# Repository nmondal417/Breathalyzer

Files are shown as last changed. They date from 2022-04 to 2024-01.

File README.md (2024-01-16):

# Breathalyzer Project Overview

The overall goal of this project is to create a wireless device that can be used to analyze the breath of medical patients to diagnose various diseases. The underlying technology is a graphene FET array. When the graphene FETs come into contact with different gases, the properties of the FETs will change. For example, the IDS vs VGS curve of the graphene FET may shift depending on the concentration of a certain gas molecule in the patient's breath. 

This GitHub project contains the PCBs and the code that are used to control and measure the graphene FET array. In simple terms, the PCB generates analog voltages VDS and VGS, and sends these to the graphene FET. Two multiplexers are used to select one particular FET out of the array. The PCB then measures the resulting IDS on that FET. This process is then repeated for every FET in the array, and then for different VDS and VGS. A python script can be used to plot the various voltage vs current curves.

functional_diagram

# Device Design

The device is split into two chambers. The top chamber contains the graphene FET chip, an interface PCB for connecting to the chip, a humdity sensor, and a heater to prevent condensation on the chip. The bottom chamber contains most of the control electronics, inlucding the ESP32 micronctroller, the amplifiers, and multiplexers. There is also a single-cell 2 Ah LiPo for powering all the electronics, and a boost converter for specifically powering the heater. The LiPo can be charged through the USB-C connector located on the bottom of the device; when charging, the device will automatically turn off. 

breathalyzer_drawing

On the outside of the device, there are various switches to control and LEDs to monitor the breathalyzer status. The main on switch connects the LiPo to the system and turns everything except the heater on; the heater on switch controls the heater. An RGB charge status LED lights up when the device is being charged; an orange light indicates that charging is occurring, while a white light indicates that charging is completed. Finally a "BLOW" LED controlled by the ESP32 indicates to the patient when they should blow into the device.

# PCBs

## ESP32 Carrier

https://github.com/nmondal417/Breathalyzer/tree/main/New%20PCB/Breathalyzer_ESP32

This PCB is where the ESP32, the main microcontroller, mounts **(NOTE: make sure to place the ESP32 correctly! the USB connector should face the side labeled "FRONT")**. The ESP32 controls the DAC, the ADC, and the multiplexers. It can also read data from the humidity sensor and the heater thermistor. It reports the current measurements in either serial or Bluetooth serial. 

The carrier board also contains the LiPo charge controller, the USB-C charging port, and the main 3.3V regulator that powers most of the ICs. All of the buttons and switches plug into the ESP32 carrrier board.

## Amplifier

https://github.com/nmondal417/Breathalyzer/tree/main/New%20PCB/Breathalyzer_Power%2BICs

This PCB contains the DAC, the ADC, and the op-amps that amplify the gate voltages.

The DAC (AD5328) communicates with the ESP32 over SPI. The DAC generates 6 gate voltages and 1 drain voltage. These voltages are in the range of 0 to 2 V; however, since the source voltage of this system is 1 V, the VGS and VDS voltages are actually -1 to +1 V. 

The op-amps then buffer and amplify the gate voltages. The op-amps can either provide x1 amplification (where it just acts a buffer), or x10 amplifcation. This amplification is controlled by the ESP32. The ESP32 controls two solid-state switches (ADG5433), which can change the amplifer gain by switching in a feedback resistor connected across the op-amp. The post-amplifcation gate voltage can be from -10 to +10 V.

The ADC (AD7274) communicates with the ESP32 over SPI. The ADC input is the voltage from the transimpedance amplifier. The ADC reads in range of 0 to 2V, and sends the ESP32 a 12-bit digital reading. 

This PCB also contains the 1V and 2V regulators that generate reference voltages for the DAC, ADC, and the op-amps, as well as a dual DC/DC converter (LT1945) that generates the -11V and +11V rails used for the amplifiers.

Finally, there is a mechanical switch that can completely disconnect the gate voltages from the graphene chip. This is useful for quickly turning off a voltage sweep, since if the incorrect gate voltages are accidentally applied the FET array can be destroyed.

## Multiplexer

https://github.com/nmondal417/Breathalyzer/tree/main/New%20PCB/Breathalyzer_Mux%2BConn

This PCB contains the two main multiplexers, the ribbon cable connector, and the transimpedance amplifier. 

The multiplexers are the ADG732. One is the drain demultiplexer, which sends the drain voltage to 1 of the 32 rows of the FET array. The other is the source muliplexer, which measures the source current from 1 of the 32 columns. 

The ribbon cable connector connects to the ribbon cable that runs from this PCB to the chip interface board. This cable is the PCB's connection to the drain, gate, and source terminals on the FET array.

The transimpedance ampliifer is an op-amp that is used to convert the source current measurement into a voltage. The formula is VMEAS = 1 - 1000*IDS, so an IDS of 100 uA would result in a VMEAS of 0.9V. This VMEAS is sent to the ADC.

# Code

All the code for this version of the breathlyzer is under 'New PCB code.' While the main code that runs on the ESP32 during normal operation is IV_Array_main_NEW, there are other files that test specific parts of the system, like the DAC and ADC, and are helpful for debugging.

## Blink

Simple test to just check if code can be uploaded correctly to the ESP32.

## ADC_DAC_test

This test can be used to test the ADC, DAC, or both together. Bascially, write analog voltages using the DAC and read an analog voltage using the ADC. If you are testing both the DAC and ADC at the same time, connect one of the DAC's output voltages to the input of the ADC.

## offset_and_gain_test

Used for checking and adjusting for the offset or gain error of the ADC and DAC. Test each DAC channel by connecting it to the ADC, and compare the read voltages to the expected values.

## gate_voltage_test

Tests that gate voltages can be generated properly. Combines the DAC code along with additional code to turn on the gate amplifier power supply and control the amplification.

## multiplexer_test

Close to a full system test, but instead of having the actual graphene array connected, you connect a test resistor between a drain connection on one mux and source connection on the other. When the correct select bits are sent to the muxes, the code should report the resistor value.

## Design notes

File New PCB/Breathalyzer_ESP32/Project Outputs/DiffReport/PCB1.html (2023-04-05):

Altium

# Differences Report for Project Breathalyzer_ESP32.PrjPcb and PCB1.PcbDoc

Date: | | 3/28/2023
Time: | | 11:31:12 PM
Filename: | | C:\college\UROP_S2022\Breathalyzer_ESP32\Project Outputs\DiffReport\PCB1.html

## Extra Room Definitions

Schematic Object | PCB Object
[Room ESP32 (Scope=InComponentClass('ESP32')) TopLayer]

Back to top

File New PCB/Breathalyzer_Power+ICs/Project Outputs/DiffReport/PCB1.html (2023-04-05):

Altium

# Differences Report for Project Breathalyzer_Power+ICs.PrjPcb and PCB1.PcbDoc

Date: | | 3/29/2023
Time: | | 1:41:04 PM
Filename: | | C:\college\UROP_S2022\Breathalyzer_Power+ICs\Project Outputs\DiffReport\PCB1.html

## Extra Room Definitions

Schematic Object | PCB Object
[Room Power+ICs (Scope=InComponentClass('Power+ICs')) TopLayer]

Back to top

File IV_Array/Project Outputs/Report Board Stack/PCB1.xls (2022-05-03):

Board Stack Report
Stack Up |  | Layer Stack
Layer | Rigid | Name | Material | Thickness | Constant
1 |  | Top Paste
2 |  | Top Overlay
3 |  | Top Solder | Solder Resist | 0.50mil | 3.3
4 |  | Top Layer | Copper | 0.70mil
5 |  | Dielectric 1 | PP-006 | 2.80mil | 4.1
6 |  | GND | Copper | 1.38mil
7 |  | Dielectric1 | FR-4 | 59.00mil | 4.3
8 |  | PWR | Copper | 1.38mil
9 |  | Dielectric 2 | PP-006 | 2.80mil | 4.1
10 |  | Bottom Layer | Copper | 0.70mil
11 |  | Bottom Solder | Solder Resist | 0.50mil | 3.3
12 |  | Bottom Overlay
13 |  | Bottom Paste
 | Height : 69.76mil

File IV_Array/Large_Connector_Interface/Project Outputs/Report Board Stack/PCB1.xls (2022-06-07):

Board Stack Report
Stack Up |  | Layer Stack
Layer | Rigid | Name | Material | Thickness | Constant
1 |  | Top Paste
2 |  | Top Overlay
3 |  | Top Solder | Solder Resist | 0.50mil | 3.3
4 |  | Top Layer | Copper | 0.70mil
5 |  | Dielectric1 | FR-4 | 59.00mil | 4.3
6 |  | Bottom Layer | Copper | 0.70mil
7 |  | Bottom Solder | Solder Resist | 0.50mil | 3.3
8 |  | Bottom Overlay
9 |  | Bottom Paste
 | Height : 61.40mil

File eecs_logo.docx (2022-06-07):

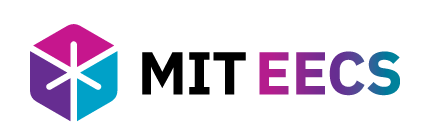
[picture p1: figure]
EECS Communication Lab

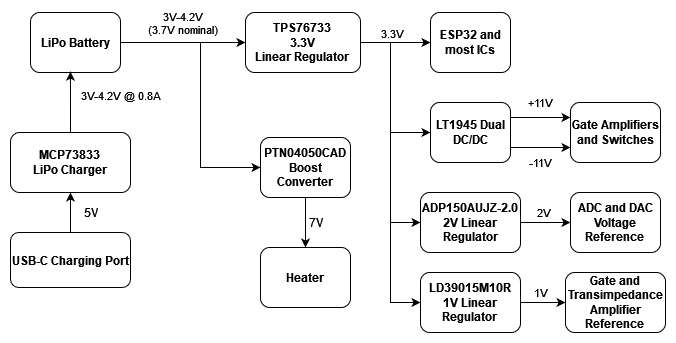
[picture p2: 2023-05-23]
power_flow.png

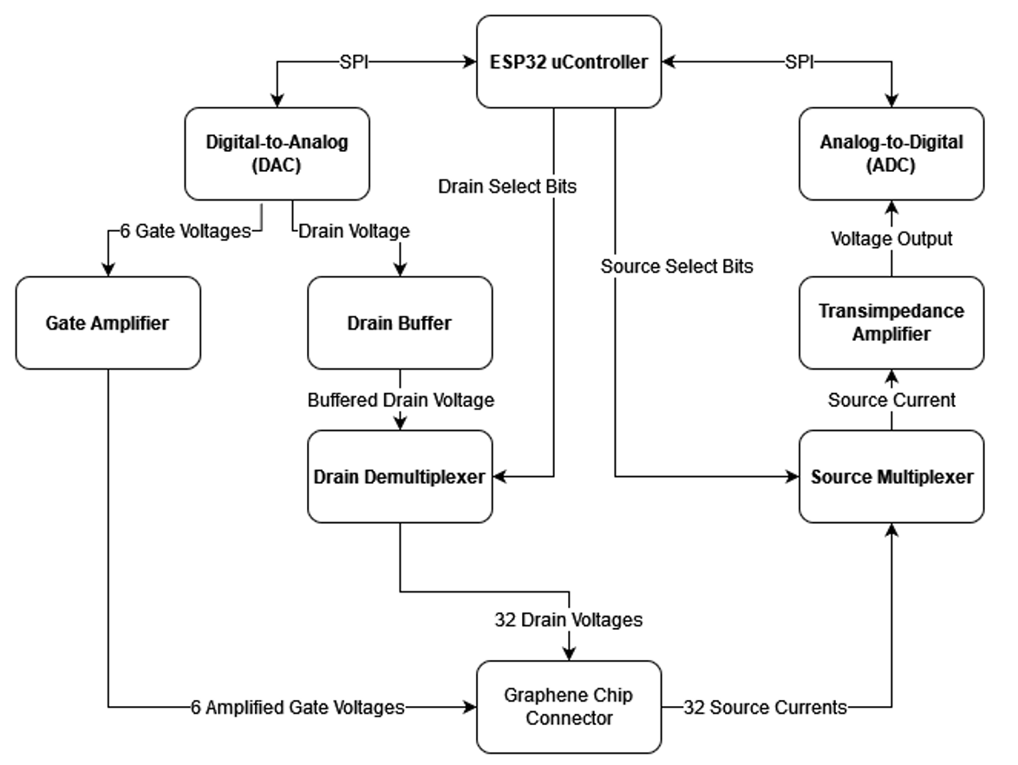
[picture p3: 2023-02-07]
functional_diagram.png

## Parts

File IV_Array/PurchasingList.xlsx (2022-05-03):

Comment | Description | Designator | Fitted | Footprint | LibRef | Quantity | Value | PN | OK? | #Bought
100 nF | CAP CER 0.1UF 50V X7R 0805 | C1, C2, C3, C4, C5, C12, C18, C19, C20, C21, C22, C23, C24, C25, C26, C27, C28 |  | FP-C0805C-DN-MFG | CMP-2007-00279-2 | 17 | 0.10 μF | C0805C104K5RACTU (https://octopart.com/c0805c104k5ractu-kemet-143926?r=sp) | Mouser | 100 | c
10 uF | CL21 Series 0805 10uF 25V ±10% Tolerance X5R Multilayer Ceramic Chip Capacitor | C6, C7, C8, C9, C10, C11 |  | FP-CL21-IPC_A | CMP-13271-002975-1 | 6 |  | CL21A106KAYNNNE | Mouser | 30 | c
100 pF | 08055C101KAT2A | C13 |  | CAPC2013X140X50ML20T25 | CMP-2007-04713-1 | 1 |  | 08055C101KAT2A (https://octopart.com/08055c101kat2a-kyocera+avx-41088415?r=sp) | Mouser | 10 | c
1 uF | C1206C105K5RACTU | C14, C16 |  | CAPC3216X110X50LL20T25 | CMP-2000-06011-1 | 2 |  | C1206C105K5RACTU | Mouser | 10 | c
4.7 uF | CAP CER 4.7UF 25V X5R 0805 | C15 |  | FP-C0805C475K3PACTU-MFG | CMP-2007-01010-2 | 1 |  | C0805C475J3RACTU | Mouser | 10 | c
4.7 pF | 08055A4R7CAT2A | C17 |  | CAPC2013X71X50ML20T25 | CMP-1036-00549-2 | 1 |  | 08055A4R7CAT2A | Mouser | 10 | c
MBR0530 | DIODE SCHOTTKY 30V 500MA SOD123 | D1, D2, D3 |  | FP-425-04-MFG | CMP-2000-05113-2 | 3 |  | MBR0530T1G | Mouser | 15 | c
FH12-36S-0.5SH_55_ | Connector | J2 |  | FH1236S05SH55 | FH12-36S-0.5SH_55_ | 1 |  |  | Already have
5015 | PC TEST POINT MINIATURE | J3, J4, J5, J6, J7, J8, J9, J11, J12, J13, J14, J15, J16, J17, J18 |  | FP-5015-MFG | CMP-2000-05183-2 | 15 |  |  | N/A
5600200620 | CONN HEADER SMD 6POS 2MM | J10 |  | FP-5600200620-MFG | CMP-04776-000066-1 | 1 |  | 560020-0620 | Mouser | 5 | c
FH28H-80S-0.5SH(05) | CONN FFC BOTTOM 80POS 0.50MM R/A | J19 |  | FP-FH28H-80S-0_5SH_05-MFG | CMP-11609-000031-1 | 1 |  |  | Already have
503366-6011 | 0.5 mm Pitch Easy-On(TM) FPC Connector, 2.0 mm Mated Height, Right Angle, SMT, Bottom Contact, 60 Circuits, -20 to 85 degC, ELV and RoHS Compliant, Tape and Reel | J20 |  | MOLX-503366-6011 | CMP-1241-00108-1 | 1 |  | 503366-6011 | Mouser | 10 | c
LQH3NPN100MMEL | Wire Wound Ferrite Inductor for Power Lines 10μH ±20% 0.228Ω 1280mA 1212 | L1, L2 |  | FP-LQH3NPH_ME-MFG | CMP-06042-002074-1 | 2 |  | LQH3NPN100MMEL | Mouser | 10 | c
Header 18 | Header, 18-Pin | P1, P3, P4, P6 |  | HDR1X18 | Header 18 | 4 |  | PRT-00115 | Mouser | 10 | c
Header 18X2 | Header, 18-Pin, Dual row | P2, P5 |  | HDR2X18 | Header 18X2 | 2 |  | PRT-14275 | Mouser | 15 | c
Header 4X2 | Header, 4-Pin, Dual row | P7, P8 |  | HDR2X4 | Header 4X2 | 2 |  |  | Mouser
Header 8X2 | Header, 8-Pin, Dual row | P9, P10 |  | HDR2X8 | Header 8X2 | 2 |  |  | Mouser
Header 3X2 | Header, 3-Pin, Dual row | P11, P12, P13, P14, P15, P16 |  | HDR2X3 | Header 3X2 | 6 |  |  | Mouser
Header 6 | Header, 6-Pin | P17 |  | HDR1X6 | Header 6 | 1 |  |  | Mouser
Header 7 | Header, 7-Pin | P18 |  | HDR1X7 | Header 7 | 1 |  |  | Mouser
10k | Chip Resistor, 10 KOhm, +/- 1%, 0.125 W, -55 to 155 degC, 0805 (2012 Metric), RoHS, Tape and Reel | R1, R10, R11, R12, R19, R20, R21, R22, R30 |  | RESC2013X60X35NL10T20 | CMP-1659-00013-4 | 9 |  | RT0805BRE0710KL | Mouser | 100 | c
365k |  | R2 |  | RESC2013X70X40NL20T20 | CMP-2001-00152-1 | 1 |  | 667-ERJ-6ENF3653V | Mouser | 10 | c
24.9k |  | R3, R4 |  | RESC2013X70X40LL20T20 | CMP-2001-00073-1 | 2 |  | ERJ-6ENF2492V | Mouser | 10 | c
380k |  | R5 |  | RESC2013X70X40ML20T20 | CMP-2001-00160-1 | 1 |  | ERJ-6ENF3833V | Mouser | 10 | c
3269W-1-104LF | TRIMMER 100K OHM 0.25W SMD | R6, R8 |  | FP-3269W-MFG | CMP-07234-000021-1 | 2 | 100kΩ | 3269W-1-104LF | Mouser | 10 | c
12k |  | R7, R9 |  | RESC2013X60X40ML20T25 | CMP-2001-00590-1 | 2 |  | ERA-6AEB123V | Mouser | 10 | c
91k |  | R13, R15, R16, R23, R24, R25 |  | RESC2013X60X40LL20T25 | CMP-2001-00677-1 | 6 |  | ERA-6AEB913V | Mouser | 30 | c
191k |  | R14, R17, R18, R26, R27, R28 |  | RESC2013X70X40ML20T20 | CMP-2001-00021-1 | 6 |  | ERJ-6ENF1913V | Mouser | 30 | c
1k | Chip Resistor, 1 KOhm, +/- 1%, 125 mW, -55 to 155 degC, 0805 (2012 Metric), RoHS, Tape and Reel | R29 |  | RESC2013X60X35ML10T20 | CMP-2100-03671-1 | 1 |  | TNPW08051K00BEEN | Mouser | 10 | c
1825255-1 | No Description Available | SW1, SW2, SW3, SW4, SW5, SW6 |  | SW3_1825255-1_TEC | 1825255-1 | 6 |  | 1825255-1 | Mouser | 25 | c
4-1825010-2 | SWITCH SLIDE 6PDT 300MA 115V | SW7 |  | FP-4-1825010-2-MFG | CMP-03405-000018-1 | 1 |  | 4-1825010-2 | Mouser | 5 | c
MCP3201-CI/SN | 2.7V 12-Bit A/D Converter with SPI Serial Interface, 8-Pin SOIC 150mil, C Performance Grade, Industrial Temperature | U1 |  | SOIC-SN8_L | CMP-0188-00469-2 | 1 |  | MCP3201-CI/SN | Mouser | 10 | c
AD5328BRUZ | Octal 12-Bit Voltage Output Digital-to-Analog Converter, 2.5 to 5.5 V, -40 to +125 degC, RU-16, Pb-Free, Tube | U2 |  | RU-16_L | CMP-0318-02011-2 | 1 |  | AD5328BRUZ-REEL7 | Mouser | 5 | c
NCP1117ST20T3G | Low-Dropout Positive Fixed Voltage Regulator, 1 A, 2.0 V Output Voltage, 0 to 125 degC, 4-Pin SOT-223 (318H-01), Pb-Free, Tape and Reel | U3 |  | ONSC-SOT-223-4-318H-01_A_V | CMP-1679-00010-1 | 1 |  | NCP1117ST20T3G | Mouser | 10 | c
LDL1117S33R | IC REG LINEAR 3.3V 1.2A SOT223 | U4 |  | FP-SOT223-0046067-IPC_C | CMP-12153-000006-1 | 1 |  | MCP1799-3302H/DB | Mouser | 10 | c
AP7365-10EG-13 | IC REG LIN 1V 600MA SOT223-3 | U5 |  | FP-SOT223-IPC_C | CMP-12756-000040-1 | 1 |  | AP7365-10EG-13 | Mouser | 10 | c
LT1945EMS#PBF | Dual Micropower DC/DC Converter with Positive and Negative Outputs, 1.2 to 15 V Vin, 10-pin SOP (MS-10), -40 to 85 degC, Pb-Free | U6 |  | LT-MS-10_N | CMP-0478-00153-1 | 1 |  | LT1945EMS#PBF | Mouser | 10 | c
ADA4522-2ARMZ | IC OPAMP ZERO-DRIFT 2 CIRC 8MSOP | U7, U10, U11, U12 |  | FP-RM-8-IPC_C | CMP-09116-000003-2 | 4 |  | ADA4522-2 | Mouser | 15 | c
LT1213CS8#TRPBF | Dual Channel, Precision, Fast Operational Amplifier, 28 MHz Typical GBW, 8.5 V/us Typical SR, 2.5 to 36 V, 8-Pin SOIC (S8-8), Commercial, Pb-Free, Reel | U8 |  | LT-S8-8_N | CMP-0359-03127-2 | 1 |  | LT1213CS8#TRPBF | Mouser | 10 | c
ADG732BSUZ-REEL | 1.8 to 5.5 V / +/-2.5 V, 4 Ohm, 32-Channel Analog Multiplexer, -40 to 85 degC, 48-pin QFP (SU-48), Reel | U9, U13 |  | ADI-SU-48_N | CMP-0798-00236-1 | 2 |  |  | Already have
Additional
 |  |  |  |  |  |  |  | 218323-1062 | Mouser | 3 | c
 |  |  |  |  |  |  |  | PRT-00116 | Mouser | 3 | c
 |  |  |  |  |  |  | jumper | 60900213421 | Mouser | 100 | c

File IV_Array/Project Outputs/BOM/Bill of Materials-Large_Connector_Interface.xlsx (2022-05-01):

Comment | Description | Designator | Fitted | Footprint | LibRef | Quantity | Value
FH28H-80S-0.5SH(05) | CONN FFC BOTTOM 80POS 0.50MM R/A | J1, J2 |  | FP-FH28H-80S-0_5SH_05-MFG | CMP-11609-000031-1 | 2

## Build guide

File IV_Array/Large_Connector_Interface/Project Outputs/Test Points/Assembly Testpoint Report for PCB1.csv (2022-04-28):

Net | Name | X Coord | Y Coord | Side | Hole Size | Type

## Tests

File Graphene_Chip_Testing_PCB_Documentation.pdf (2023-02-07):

# Graphene Chip Tester PCB Documentation

Neel Mondal

December 9, 2022

## 1 PCB Block Diagram

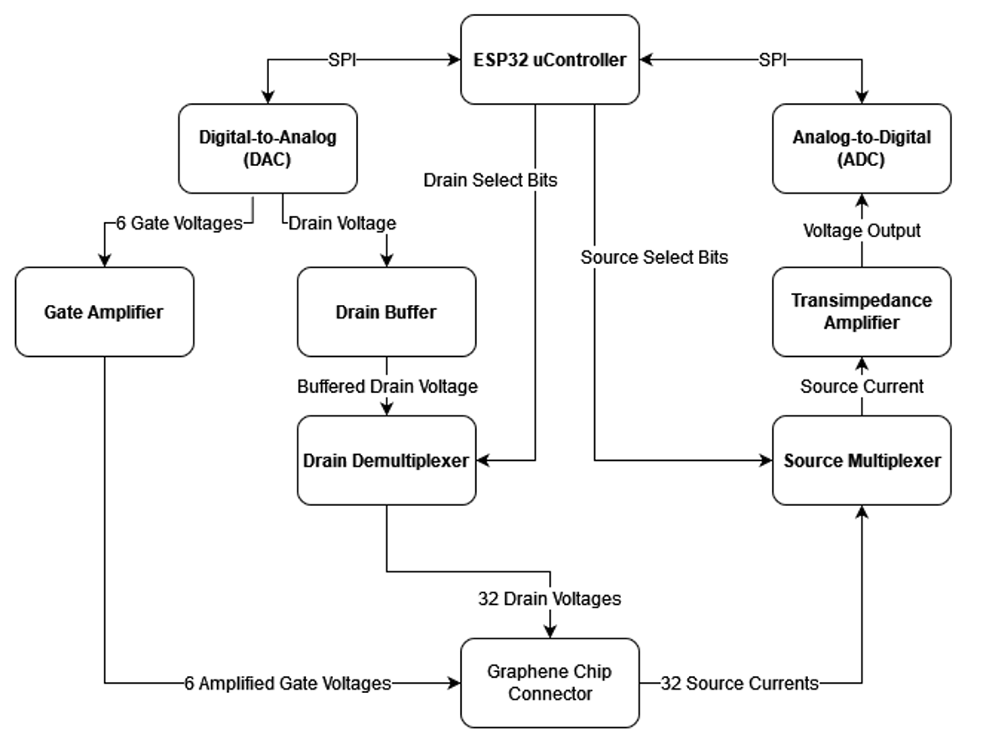
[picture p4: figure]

## 2 PCB Input and Output Specs

Supply Voltage | VGS Range | VDS Range | IDS Resolution | IDS Range
5V (from USB) | −1V to +1V (pre-amplification) −21V to +19V (w/ amplification*) | −1V to +1V | 0.49µA | −0.98mA to 0.96mA

*Positive and negative VGS thresholds can be adjusted lower using the gate potentiometers to protect

the chip from dangerous voltages.

1

## 3 Chief Components

### 3.1 Microprocessor

The microcontroller on this PCB is an ESP32-DEVKIT V1-DOIT. The ESP32 was chosen because it

has many GPIO pins, several hardware SPI peripherals, and integrated WiFi, the last of which would

be useful for a wireless version of this PCB. Compared to the Arduino Due, which was being used on

a previous version of this PCB, the ESP32 has a faster clock speed (84 vs 240 MHz) and a much lower

cost. The faster clock speed means faster digital reads and writes on GPIO pins. From testing, the

ESP32 can toggle a GPIO pin on and off using digitalWrite 1 million times in 273 ms (so a single toggle

takes on average 273 ns).

The ESP32 is powered by 5V from USB. On this PCB, the ESP32 has two main functions: interfacing

with the ADC and DAC, and controlling the two multiplexers. For the ADC and the DAC, the ESP32

uses its VSPI interface for MOSI, MISO, and SCK, and two extra GPIO pins for selecting the two

chips. For each multiplexer, the ESP32 uses 5 GPIO pins for choosing 1 of the 32 multiplexer channels,

as well as 1 extra GPIO for enabling the multiplexer.

A small modification was made to the ESP32: a 100nF capacitor was soldered from the EN pin to

GND. This enables us to flash the ESP32 without having to press the BOOT button each time.

### 3.2 Voltage References

There are several voltage regulators on the PCB, all of which take 5V from USB as input. The table

below lists all the voltage regulators:

Voltage | Part No. | Use
1V | AP7365-10EG-13 | Voltage reference for gate amplifiers and transimpedance amp
2V | NCP1117ST20T3G | Voltage reference for ADC and DAC
3.3V | LDL1117S33R | Power for ADC, DAC, multiplexers, transimpedance and drain buffer op-amp
±20V | LT1945EMS#PBF | Powering gate amplifier and gate threshold op-amps

One issue that came up during testing the PCB was that the voltage output of the 1V regulator was

not staying at 1V, instead jumping as high as 2V. The issue is that the gate amplifier op-amps on the

PCB are trying to sink a small amount of current (about 1 mA) into the 1V regulator. However, the 1V

regulator chosen cannot handle any amount of sink current. Therefore, this issue was solved by placing

2

a 1kΩ resistor from 1V to GND to draw some current, so there there would be a net source current from

the 1V regulator.

### 3.3 Digital to Analog Converter (DAC)

The DAC on this PCB is the AD5328BRUZ. This is a 12-bit DAC with 8 analog output channels,

although on this board only 7 channels are used: 6 for gate voltages, and 1 for the drain voltage. The

DAC is given a voltage reference of 2V, so it can produce voltages between 0V and 2V, in increments of

2
2

12 ≈ 0.49 mV. Since the source of the graphene FETs is 1V, this allows for equal positive and negative

VDS and VGS swing. The DAC interfaces with the ESP32 via SPI; MOSI from the ESP32 is connected

to the DIN pin of the DAC, which is used to write serial data to the DAC’s input registers.

Two additional pins on the DAC are SY NC and LDAC. When SY NC goes low, the DAC begins

reading serial data from the DIN pin, so this pin is connected to the DAC Chip Select pin on the

ESP32. Meanwhile, pulsing LDAC low transfers the contents of the DAC’s input registers to its output

pins. Therefore, LDAC is connected to a separate GPIO on the ESP32, which is pulsed low whenever

we want to update all the DAC outputs at once.

### 3.4 Multiplexers

There are two analog multiplexers on this PCB, both of which are the ADG732BSUZ. The drain

(de)multiplexer connects the buffered drain voltage from the DAC to 1 of 32 drain connections on

the graphene chip. The source multiplexer connects 1 of 32 source connections from the graphene chip

to the transimpedance amplifier. If the graphene chip being tested has less than 32 drain and source

connections, the code can be modified so that only some of the channels are addressed. For example,

for a smaller 16x16 graphene chip, the code sets A4 (the most significant address bit) low for both

multiplexers.

Since the transimpedance amplifier will be measuring IDS current from the source connection, it is

important that the impedance of the multiplexers is much lower than the impedance of our graphene

FETs, or else the measured current would be lower than expected. For a 3V supply, the typical on-

resistance of each ADG732 is 7Ω, while the impedance of the FETs is around 1000Ω. Therefore, the

error in our current measurement will be around 14
1000 = 1.4%. Another important spec is the switching

frequency of the multiplexers. For a 3V supply, the ADG732 has max output transition time of 62 ns,

so we can theoretically switch the drain and source channels at up to 16MHz. On the actual PCB, we

are limited by the GPIO read/write speed of the ESP32.

3

### 3.5 Gate Amplifiers

The VGS voltages produced by the DAC have a range from -1V to +1V. Op-amps on the PCB allow us

to choose to amplify each gate voltage by either 1X, 10X, 20X (the 1X simply acts as a buffer). This is

done through a non-inverting topology, shown below.

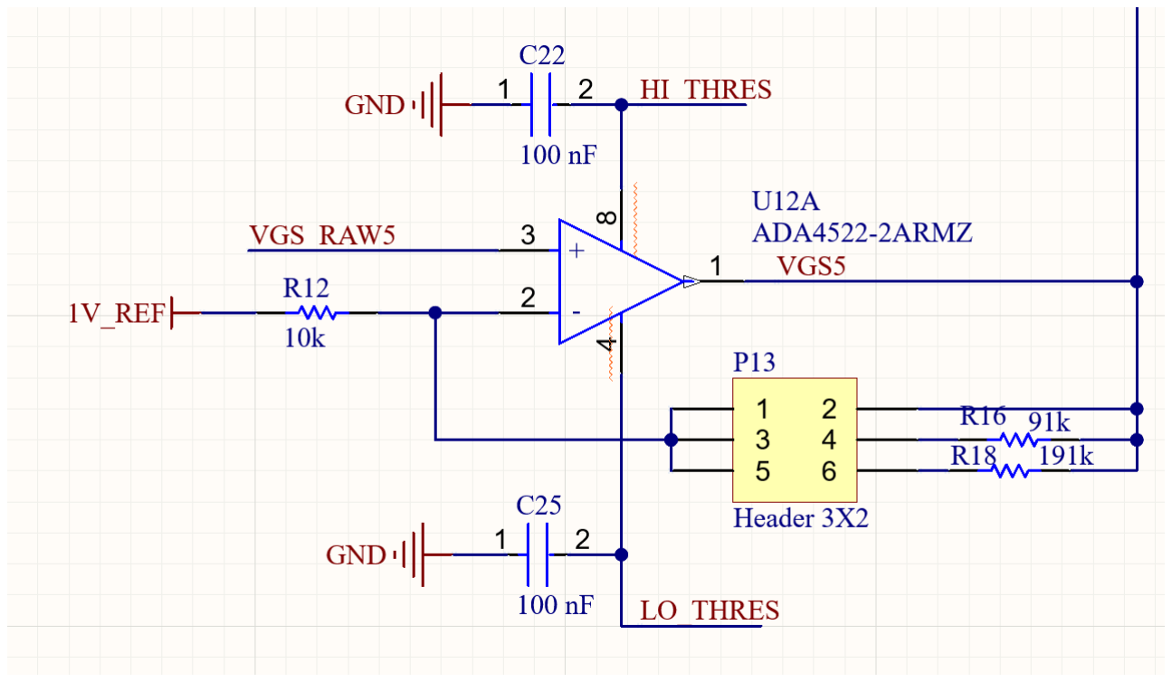
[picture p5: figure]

To choose our desired amplification, we place a jumper in one of three locations on the 3x2 header.

This jumper will either put a 91k resistor between the op amp’s inverting input and its output (for

x10 amplification), a 191k resistor (for x20 amplification), or directly connect input to output (for x1

amplification).

### 3.6 Gate Potentiometers

The gate amplifiers can amplify the VGS voltages up to -21V to +19V. However, some graphene chips that

we test might not be able to handle these high voltages, and could get damaged if the wrong amplification

is accidentally set. To prevent this, we can adjust high and low VGS thresholds by adjusting two

potentiometers on the PCB. Adjusting these potentiometers changes the voltage output of two resistor

dividers. These voltages are buffered and then used to power the supply rails of the gate amplification

op-amps. Because the op-amp cannot produce a voltage higher than its positive supply rail or lower than

its negative supply rail, the potentiometers can be used to limit the voltage range of the gate amplifiers.

The high VGS threshold can be set anywhere from +19V to +1.14V, while the low VGS threshold

can be set from -21V to -3.14V. The difference in the high and low ranges is due to the fact that the

source voltage is at 1V. To check that the VGS thresholds are properly set, the user should measure

4

each voltage threshold with respect to the 1V reference (i.e. red lead of the multimeter on the threshold

voltage, black lead on 1V reference).

### 3.7 Gate Switches

As an additional failsafe measure, if the user wishes to immediately turn off any of the gate voltages,

there are mechanical switches on the PCB that allow them to do so. These are single-pole, double-throw

switches. The ”on” configuration passes the amplified gate voltage directly to the gate on the graphene

chip, while the ”off” configuration passes a 1V reference instead. Since the source voltage is 1V with

respect to the ground, turning the switch ”off” sets the VGS of that gate to 0V.

### 3.8 Transimpedance Amplifier

A transimpedance amplifier is current to voltage converter, and the one on this PCB is implemented

using the OPA2388IDR rail-to-rail op-amp. It converts the IDS current coming into the op-amp’s

inverting input into a voltage output of 1 − 1000IDS. Therefore, this transimpedance amplifier has a

gain of 1000V/A. This gain is set by a 1k resistor between the inverting input and the output of the op-

amp. Having the op-amp be rail-to-rail is important since it allows us to measure the maximum possible

current; otherwise, the voltage output of the op-amp would saturate at a lower measured current.

During initial testing with the PCB, there was a large amount of variation in the measured current

across the different FETs of the graphene chip. This issue was fixed by placing a compensation capacitor

is parallel with the gain resistor of the transimpedance amplifier. This capacitor helps attenuate high-

frequency noise, since the new gain of the amplifier is

ZR||ZC =

R
1 + jωRC

By trial and error, the compensation capacitor was set to 330 pF. This gives our amplifier a pole at

1
2πRC ≈ 482 kHz.

### 3.9 Analog to Digital Converter (ADC)

The ADC on this PCB is the MCP3201. This is a 12-bit ADC. The ADC is given a voltage reference

of 2V, so it can read analog voltages between 0V and 2V, with a resolution of 2
2

12 ≈ 0.49 mV. The

ADC is taking in the analog voltage from the transimpedance amplifier, and outputting serial data on

5

its DOUT pin whenever its chip select pin CS is pulled low. Therefore, DOUT is connected to MISO

on the ESP32, and CS is connected the ESP32’s ADC Chip Select pin.

### 3.10 Maximum and Minimum IDS

IDS is converted into a voltage by the transimpedance amplifier, and then converted from an analog

voltage to a digital serial output by the DAC. The miminmum detectable IDS is limited by the DAC.

The DAC can measure voltages with a resolution of 0.49 mV. Since the transimpedance amplifier has a

gain of 1000, this means the current resolution is 0.49 µA. The DAC can have up to ±2 bits of offset

error and ±1 bits of gain error, so the smallest IDS we can reliably measure is around 3 µA.

The maximum positive IDS measurable is limited by the transimpedance amplifier’s output voltage

swing. When the negative supply rail of the OPA2388IDR connected to ground, the op-amp can produce

voltages as low as 40 mV. Since the equation for our transimpedance amplifier is 1−1000IDS, this means

the maximum IDS measurable is 0.96 mA.

The maximum negative IDS measurable is limited by the DAC’s reference voltage of 2V. This limits

the maximum negative IDS to −1 mA (in practice, around −0.98 mA).

6

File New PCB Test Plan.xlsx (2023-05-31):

Important Things to Remember
Plug in ESP32 properly (USB side is facing the side labeled "FRONT"
Do not turn the ON switch on and plug into the ESP32 USB at the same time
Test Name | Test Procedure | Criteria for Success | Completed | Notes
Power rails. | Plug the three main PCBs together. Hook up power supply set to 3.7V to VBATT and turn on main power switch. Measure the power rails. Then sweep power supply input from 3V to 4.2V. | 1V, 2V, and 3V3 rails all are close to their expected value. VIN should be around 3.3V due to reverse diode. +-11V rails should be off. Current consumption looks ok (<100 mA). LOWBATT signal should go low once input is below 3.3V. |  | Current draw is 13 mA at 3.7V. +11V rail is at around 3V, -11v rail is at 0.5V. !V rail is at 0.993V, 2V rail is at 2.004V. LOWBATT triggers at 3.15V.
LiPo | Disconnect power supply, connect LiPo instead. Measure the power rails again. | Voltages are as expected from the previous test.
USB Charging | Connect USB-C to PCB to charge the LiPo. | Voltage rails should turn off. Max charging current should be around 0.8A. Charge LED should turn on (orange). Voltage of battery slowly increases. When charging is done, charge LED turns white.
ESP32 Basic Test | Connect ESP32 and run Blink. | ESP32 blinks the ON LED.
DAC Test | Run ADC_DAC_test on ESP32. Run for every channel of the DAC. | Measured DAC voltages (VGSRAW and VDSRAW) are consistent with what is reported in serial.
ADC Test | Using a breadboard, connect a potentiometer and resistor between the 2V reference rail and GND to create a resistor divider. Feed the output of the resistor divider into VMEAS. Run ADC_DAC_test. | Vary VMEAS by turning the potentiometer around. Probe VMEAS, it should be close to what the ADC is reporting. |  | Bottom PCB has to be disconnected for this test.
DAC and ADC test | Feed the ouput of one of the DAC channels into VMEAS. Run ADC_DAC_test for every channel. | ADC's reported voltage is consistent with what is being written to the DAC. |  | Bottom PCB has to be disconnected for this test. | (positive offset means measured is higher than expected) Channel 0: +20mV, Channel 1: -5mV, Channel 2: +20 mV, Channel 3: no offset, Channel 4: +10 mV, Channel 5: no offset, Channel 6: -5 mV
Gate Voltage Power Rails | Run gate_voltage_test. Test the +-11V power rails. | The +-11V power rails are now on.
Gate Voltage Test, x1 | Run gate_voltage_test with x1 amplification. | Gate voltages measured from a multimeter are consistent with what the gate_voltage_test is reporting in serial.
Gate Voltage Test, x10 | Run gate_voltage_test with x10 amplification. | Gate voltages measured from a multimeter are consistent with what the gate_voltage_test is reporting in serial.
Gate Switch Test | Flip the global gate switch while running gate_voltage_test. | All gate voltages turn off.
Transimpedance Amplifier Test | Solder wires to VDS_BUFF and IDS. Connect these wires to a breadboard with a resistor (>= 1k) in between. Run transimpedance_test, updating test_resistor with whatever resistance was used. | Current expected and current measured are about the same.
Drain Demultiplexer Test | Run multiplexer_test. Test the drain demultiplexer at addresses 0 and 31, measure voltage at VDS1 and VDS32. | With code set to address 0, Vds voltage is observed at VDS1. With code set to address 31, Vds voltage is observed at VDS32.
Source Multiplexer Test | Run multiplexer_test. Test the source multiplexer by choosing addresses 0 and 31 and supplying either IDS1 or IDS31 with an analog voltage (like from a resistor divider). | ADC voltage reported changes as voltage of the chosen mux input changes (not that ADC voltage will not be equal to the mux input voltage)
Demux+Mux Test | Run multiplexer_test.ino. Solder wires to drain 31 and source 31, connect these to a breadboard with a test resistor (>= 1k) in between. (Basically the Transimpedance test but now with the multiplexers in between). | Current expected and current measured are about the same.
Final Test | Run final_boss. Try out Vds sweeps, Vgs sweeps, Vgs amplifcations, etc all at once. | Vgs voltages are what we expect them to be, current readings from transimpedance amplifer are accurate, power rails are stable.
Test Name | Test Procedure | Criteria for Success | Completed | Notes
Boost converter | Hook up boost converter to main PCB assembly. Test heater voltage output. | Before the heater is turned on, the output should be 0V. When heater is turned on, the output is about 7V. Heater ON LED turns on.
Heater | Connect heater to boost converter. Check temperature. (WARNING: Heater gets very hot!) | Heater should rise to about 100C within a few minutes.
Temp Check | Attach thermistor to the side of the heater, and connect the thermistor to the ESP32 Carrier PCB (HEAT THERM header) | ESP32 serial reports correct thermistor readings.
Test Name | Test Procedure | Criteria for Success | Completed | Notes
Humidity Sensor | Connect BME680 to main PCB assembly. Run BME680_test. | Serial reports reasonable temp readings and humidity readings. When you breathe on the sensor, the humidity and temperature should rise.

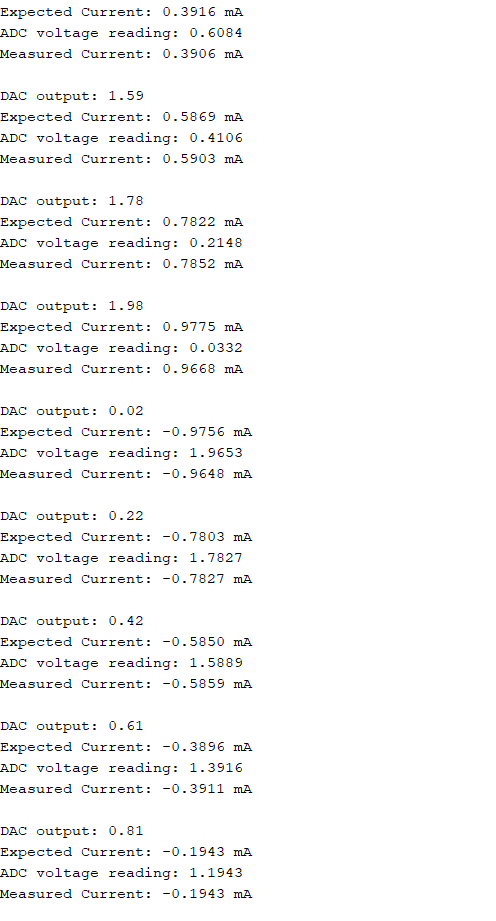
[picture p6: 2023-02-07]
transimp_test_results.png

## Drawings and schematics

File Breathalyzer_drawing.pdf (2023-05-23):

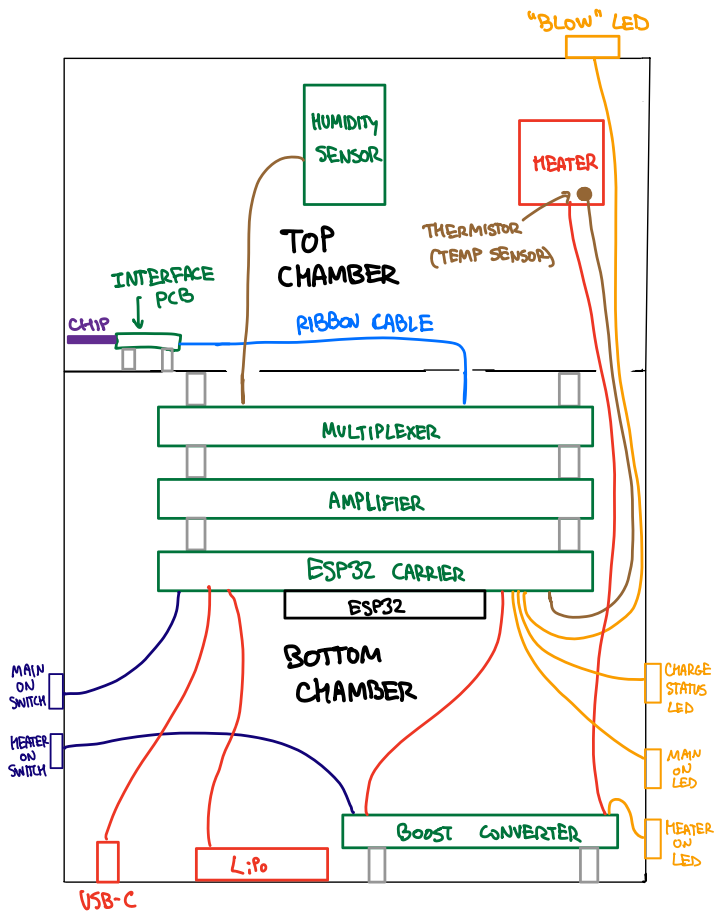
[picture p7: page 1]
HUMIDITY; SENSOR; HEATER; TOP CHAMBER; TEMPSENSOR; MULTIPLEXER; AMPLIFIER; ESP32 CARRIER; ESP32; BOTTOM

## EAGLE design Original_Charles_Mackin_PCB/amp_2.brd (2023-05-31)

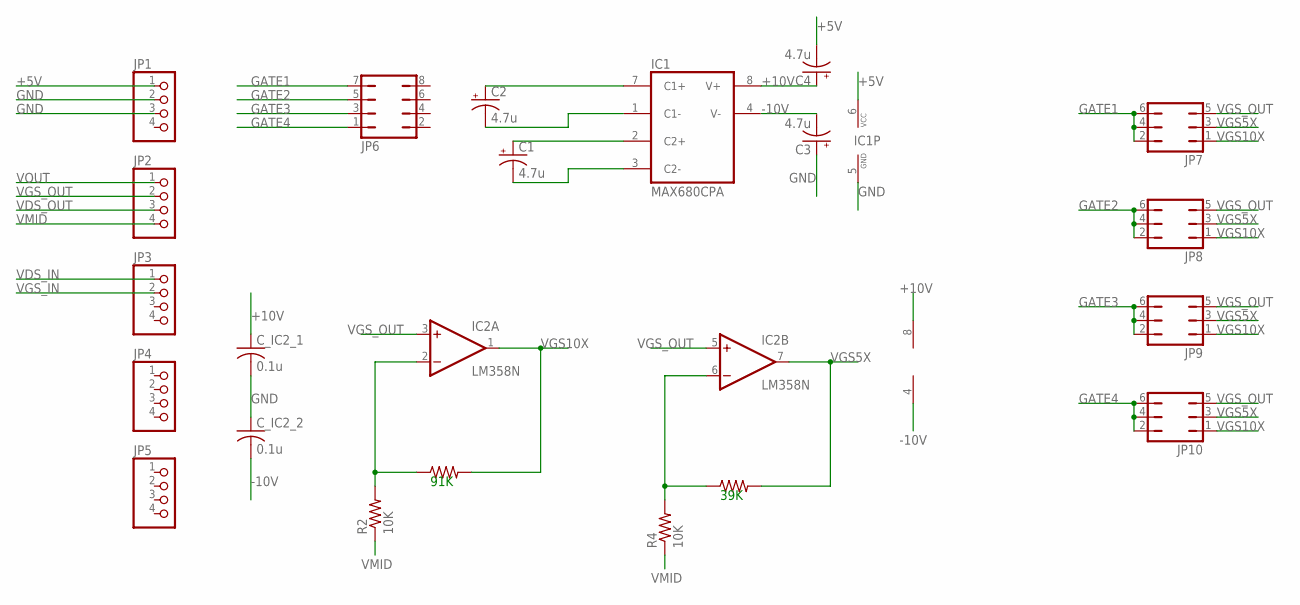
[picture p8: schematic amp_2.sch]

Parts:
C1, C2, C3, C4: 4.7u; B45181B
C_IC2_1, C_IC2_2: 0.1u; C025-024X044
IC1: MAX680CPA; DIL08
IC2: LM358N; DIL08
JP1, JP2, JP3, JP4, JP5: PINHD-1X4; 1X04
JP6: JP4Q
JP7, JP8, JP9, JP10: JP3Q
R1: 91K; 0204/7
R2, R4: 10K; 0204/7
R3: 39K; 0204/7

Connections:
+5V: C4.-, IC1.6 (VCC), JP1.1
+10V: C4.+, C_IC2_1.1, IC1.8 (V+), IC2.8 (V+)
-10V: C3.-, C_IC2_2.2, IC1.4 (V-), IC2.4 (V-)
GATE1: JP6.7, JP7.2, JP7.4, JP7.6
GATE2: JP6.5, JP8.2, JP8.4, JP8.6
GATE3: JP6.3, JP9.2, JP9.4, JP9.6
GATE4: JP6.1, JP10.2, JP10.4, JP10.6
GND: C3.+, C_IC2_1.2, C_IC2_2.1, IC1.5 (GND), JP1.2, JP1.3
unnamed: C2.+, IC1.7 (C1+)
unnamed: C2.-, IC1.1 (C1-)
unnamed: C1.+, IC1.2 (C2+)
unnamed: C1.-, IC1.3 (C2-)
unnamed: IC2.2 (-IN), R1.1, R2.2
unnamed: IC2.6 (-IN), R3.1, R4.2
VDS_IN: JP3.1
VDS_OUT: JP2.3
VGS5X: IC2.7 (OUT), JP7.3, JP8.3, JP9.3, JP10.3, R3.2
VGS10X: IC2.1 (OUT), JP7.1, JP8.1, JP9.1, JP10.1, R1.2
VGS_IN: JP3.2
VGS_OUT: IC2.3 (+IN), IC2.5 (+IN), JP2.2, JP7.5, JP8.5, JP9.5, JP10.5
VMID: JP2.4, R2.1, R4.1
VOUT: JP2.1

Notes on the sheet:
91K
39K

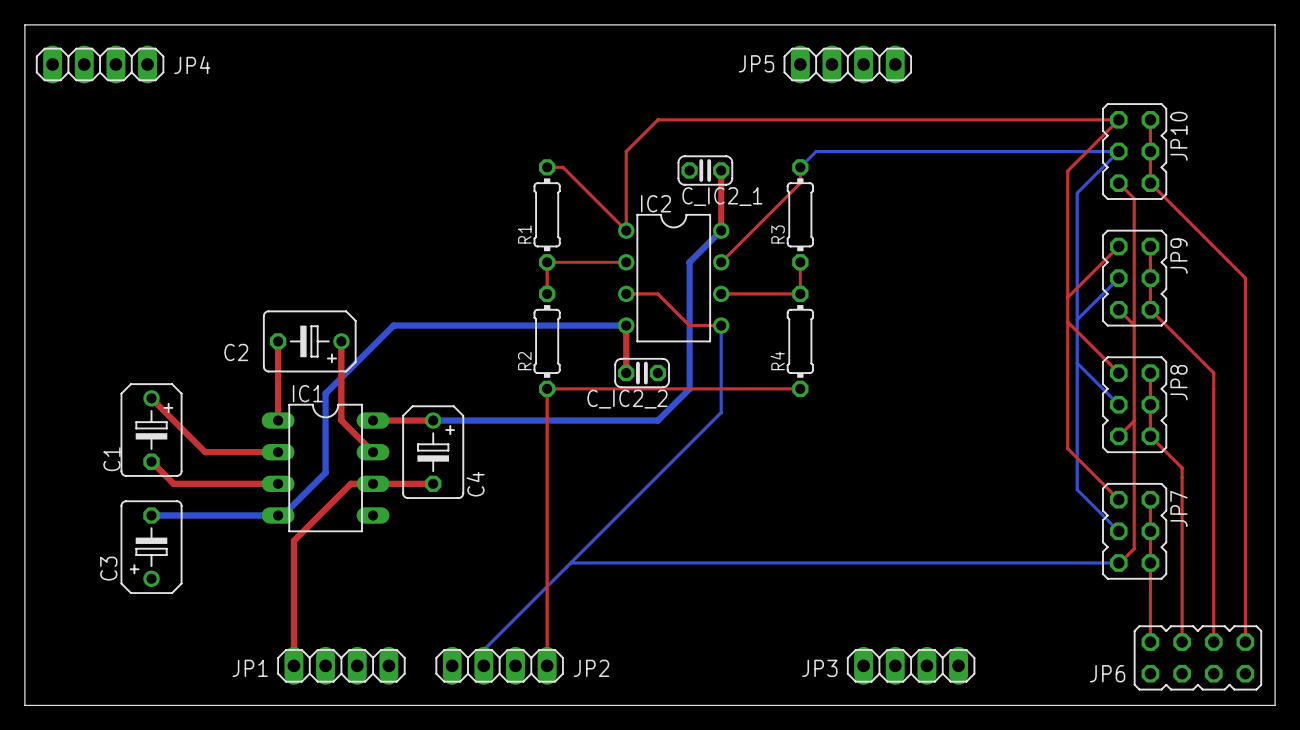
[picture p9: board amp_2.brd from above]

Board: 2 copper layers, 100.3 x 54.6 mm, 22 parts (0 on the bottom side), 18 nets.

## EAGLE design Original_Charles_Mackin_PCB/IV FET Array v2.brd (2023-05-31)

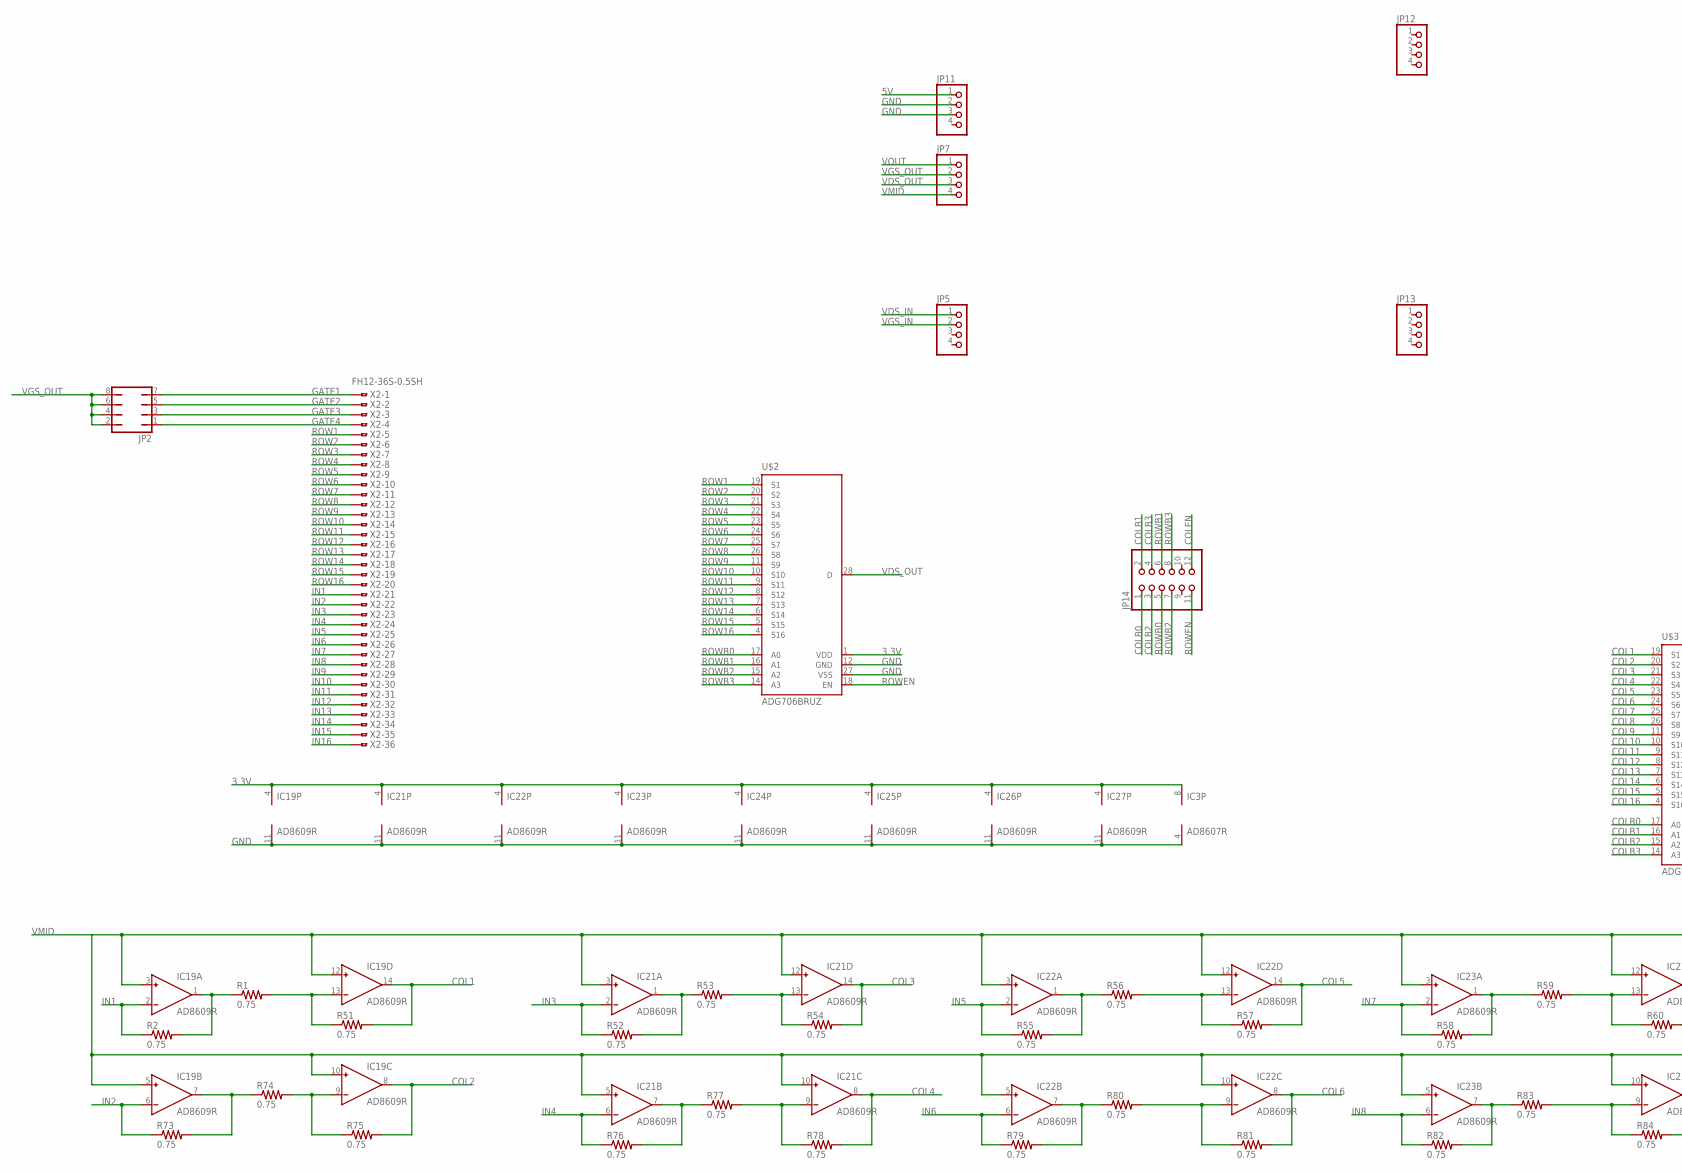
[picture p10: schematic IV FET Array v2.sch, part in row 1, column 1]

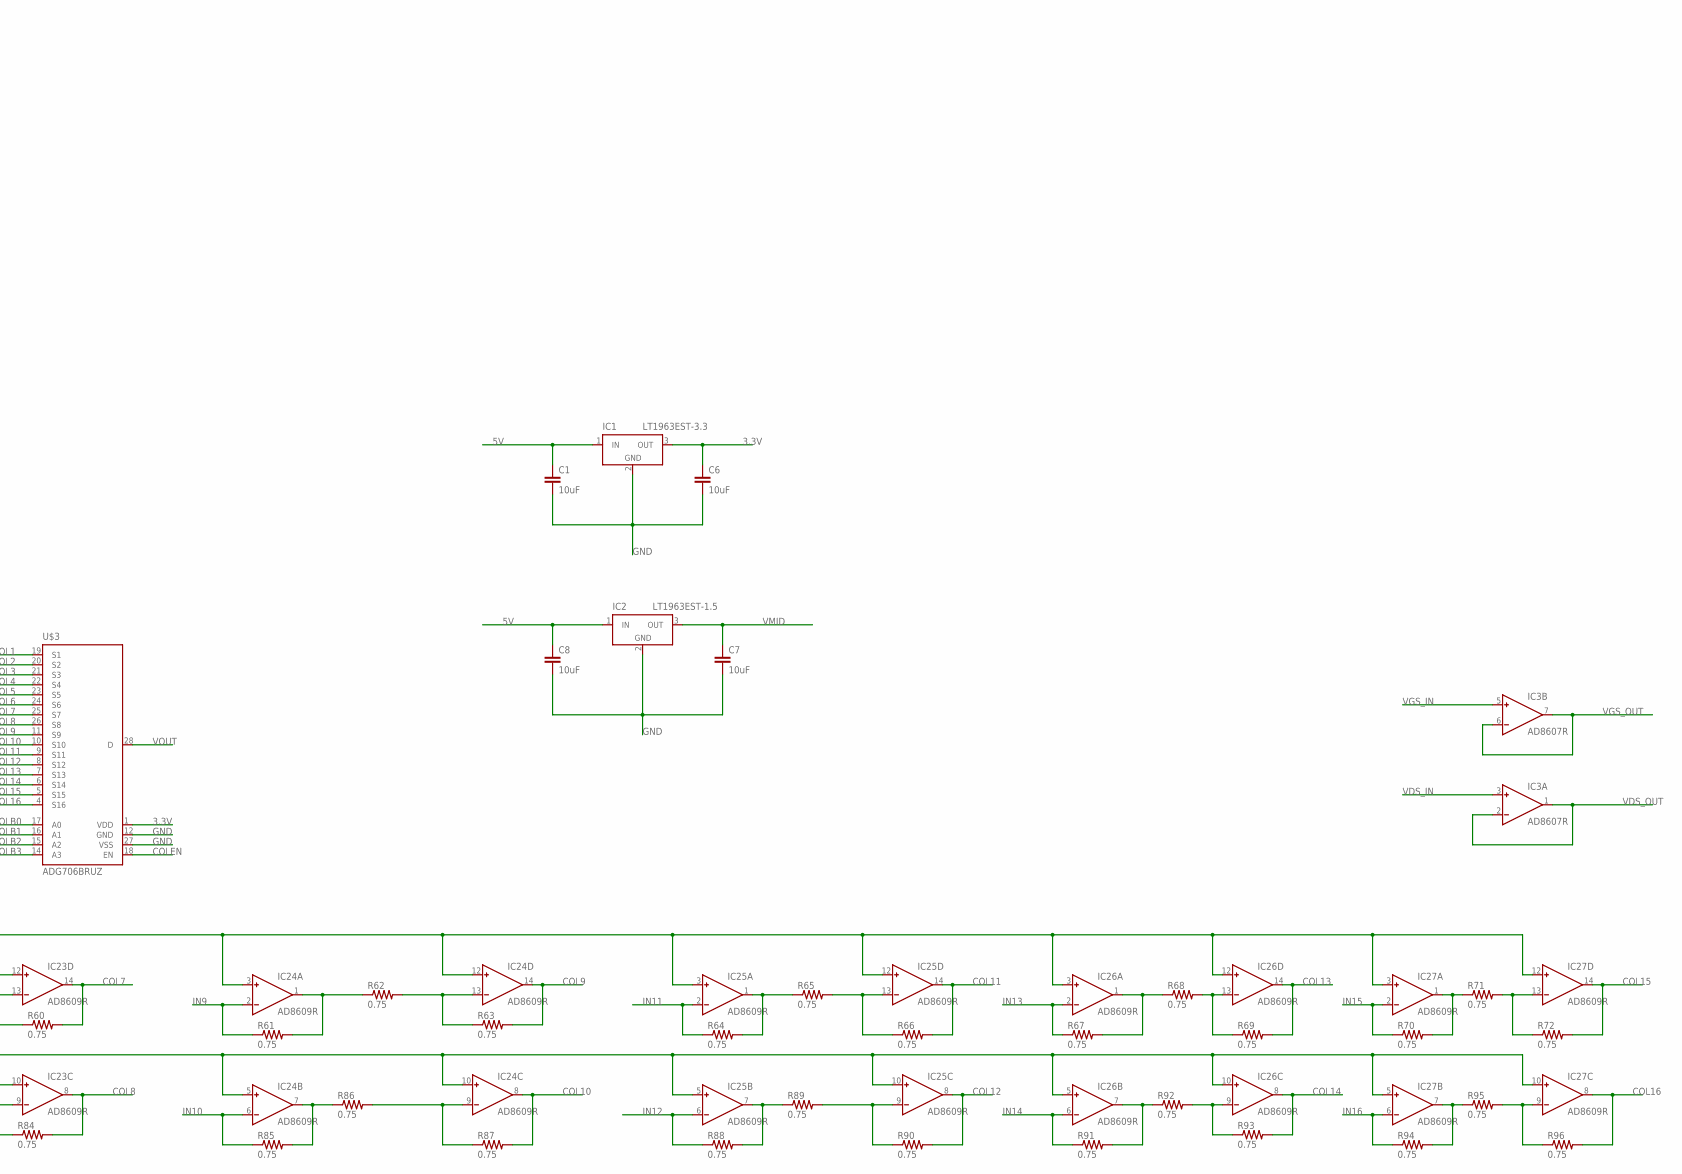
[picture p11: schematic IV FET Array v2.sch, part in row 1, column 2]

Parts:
C1, C6, C7, C8: 10uF; 1210
IC1: LT1963EST-3.3; SOT223
IC2: LT1963EST-1.5; SOT223
IC3: AD8607R; SO8
IC19, IC21, IC22, IC23, IC24, IC25, IC26, IC27: AD8609R; SO14
JP2: JP4Q
JP5, JP7, JP11, JP12, JP13: PINHD-1X4; 1X04
JP14: PINHD-2X6; 2X06
R1, R2, R51, R52, R53, R54, R55, R56, R57, R58, R59, R60, R61, R62, R63, R64, R65, R66, R67, R68, R69, R70, R71, R72, R73, R74, R75, R76, R77, R78, R79, R80, R81, R82, R83, R84, R85, R86, R87, R88, R89, R90, R91, R92, R93, R94, R95, R96: 0.75; 0805
U$2, U$3: ADG706BRUZ; TSSOP28
X2: FH12-36S-0.5SH

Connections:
3.3V: C6.1, IC1.3 (OUT), IC3.8 (V+), IC19.4 (V+), IC21.4 (V+), IC22.4 (V+), IC23.4 (V+), IC24.4 (V+), IC25.4 (V+), IC26.4 (V+), IC27.4 (V+), U$2.1 (VDD), U$3.1 (VDD)
5V: C1.1, C8.1, IC1.1 (IN), IC2.1 (IN), JP11.1
COL1: IC19.14 (OUT), R51.2, U$3.19 (S1)
COL2: IC19.8 (OUT), R75.2, U$3.20 (S2)
COL3: IC21.14 (OUT), R54.2, U$3.21 (S3)
COL4: IC21.8 (OUT), R78.2, U$3.22 (S4)
COL5: IC22.14 (OUT), R57.2, U$3.23 (S5)
COL6: IC22.8 (OUT), R81.2, U$3.24 (S6)
COL7: IC23.14 (OUT), R60.2, U$3.25 (S7)
COL8: IC23.8 (OUT), R84.2, U$3.26 (S8)
COL9: IC24.14 (OUT), R63.2, U$3.11 (S9)
COL10: IC24.8 (OUT), R87.2, U$3.10 (S10)
COL11: IC25.14 (OUT), R66.2, U$3.9 (S11)
COL12: IC25.8 (OUT), R90.2, U$3.8 (S12)
COL13: IC26.14 (OUT), R69.2, U$3.7 (S13)
COL14: IC26.8 (OUT), R93.2, U$3.6 (S14)
COL15: IC27.14 (OUT), R72.2, U$3.5 (S15)
COL16: IC27.8 (OUT), R96.2, U$3.4 (S16)
COLB0: JP14.1, U$3.17 (A0)
COLB1: JP14.2, U$3.16 (A1)
COLB2: JP14.3, U$3.15 (A2)
COLB3: JP14.4, U$3.14 (A3)
COLEN: JP14.12, U$3.18 (EN)
GATE1: JP2.7, X2.1
GATE2: JP2.5, X2.2
GATE3: JP2.3, X2.3
GATE4: JP2.1, X2.4
GND: C1.2, C6.2, C7.2, C8.2, IC1.2 (GND), IC1.4 (GND), IC2.2 (GND), IC2.4 (GND), IC3.4 (V-), IC19.11 (V-), IC21.11 (V-), IC22.11 (V-), IC23.11 (V-), IC24.11 (V-), IC25.11 (V-), IC26.11 (V-), IC27.11 (V-), JP11.2, JP11.3, U$2.12 (GND), U$2.27 (VSS), U$3.12 (GND), U$3.27 (VSS)
IN1: IC19.2 (IN-), R2.1, X2.21
IN2: IC19.6 (IN-), R73.1, X2.22
IN3: IC21.2 (IN-), R52.1, X2.23
IN4: IC21.6 (IN-), R76.1, X2.24
IN5: IC22.2 (IN-), R55.1, X2.25
IN6: IC22.6 (IN-), R79.1, X2.26
IN7: IC23.2 (IN-), R58.1, X2.27
IN8: IC23.6 (IN-), R82.1, X2.28
IN9: IC24.2 (IN-), R61.1, X2.29
IN10: IC24.6 (IN-), R85.1, X2.30
IN11: IC25.2 (IN-), R64.1, X2.31
IN12: IC25.6 (IN-), R88.1, X2.32
IN13: IC26.2 (IN-), R67.1, X2.33
IN14: IC26.6 (IN-), R91.1, X2.34
IN15: IC27.2 (IN-), R70.1, X2.35
IN16: IC27.6 (IN-), R94.1, X2.36
unnamed: IC25.1 (OUT), R64.2, R65.1
unnamed: IC25.13 (IN-), R65.2, R66.1
unnamed: IC24.1 (OUT), R61.2, R62.1
unnamed: IC24.13 (IN-), R62.2, R63.1
unnamed: IC25.7 (OUT), R88.2, R89.1
unnamed: IC25.9 (IN-), R89.2, R90.1
unnamed: IC24.9 (IN-), R86.2, R87.1
unnamed: IC24.7 (OUT), R85.2, R86.1
unnamed: IC19.1 (OUT), R1.1, R2.2
unnamed: IC19.7 (OUT), R73.2, R74.1
unnamed: IC19.9 (IN-), R74.2, R75.1
unnamed: IC19.13 (IN-), R1.2, R51.1
unnamed: IC23.13 (IN-), R59.2, R60.1
unnamed: IC23.1 (OUT), R58.2, R59.1
unnamed: IC21.1 (OUT), R52.2, R53.1
unnamed: IC21.13 (IN-), R53.2, R54.1
unnamed: IC22.1 (OUT), R55.2, R56.1
unnamed: IC22.13 (IN-), R56.2, R57.1
unnamed: IC23.9 (IN-), R83.2, R84.1
unnamed: IC23.7 (OUT), R82.2, R83.1
unnamed: IC22.9 (IN-), R80.2, R81.1
unnamed: IC22.7 (OUT), R79.2, R80.1
unnamed: IC21.9 (IN-), R77.2, R78.1
unnamed: IC21.7 (OUT), R76.2, R77.1
unnamed: IC26.1 (OUT), R67.2, R68.1
unnamed: IC26.13 (IN-), R68.2, R69.1
unnamed: IC26.9 (IN-), R92.2, R93.1
unnamed: IC26.7 (OUT), R91.2, R92.1
unnamed: IC27.7 (OUT), R94.2, R95.1
unnamed: IC27.9 (IN-), R95.2, R96.1
unnamed: IC27.13 (IN-), R71.2, R72.1
unnamed: IC27.1 (OUT), R70.2, R71.1
ROW1: U$2.19 (S1), X2.5
ROW2: U$2.20 (S2), X2.6
ROW3: U$2.21 (S3), X2.7
ROW4: U$2.22 (S4), X2.8
ROW5: U$2.23 (S5), X2.9
ROW6: U$2.24 (S6), X2.10
ROW7: U$2.25 (S7), X2.11
ROW8: U$2.26 (S8), X2.12
ROW9: U$2.11 (S9), X2.13
ROW10: U$2.10 (S10), X2.14
ROW11: U$2.9 (S11), X2.15
ROW12: U$2.8 (S12), X2.16
ROW13: U$2.7 (S13), X2.17
ROW14: U$2.6 (S14), X2.18
ROW15: U$2.5 (S15), X2.19
ROW16: U$2.4 (S16), X2.20
ROWB0: JP14.5, U$2.17 (A0)
ROWB1: JP14.6, U$2.16 (A1)
ROWB2: JP14.7, U$2.15 (A2)
ROWB3: JP14.8, U$2.14 (A3)
ROWEN: JP14.11, U$2.18 (EN)
VDS_IN: IC3.3 (IN+), JP5.1
VDS_OUT: IC3.1 (OUT), IC3.2 (IN-), JP7.3, U$2.28 (D)
VGS_IN: IC3.5 (IN+), JP5.2
VGS_OUT: IC3.6 (IN-), IC3.7 (OUT), JP2.2, JP2.4, JP2.6, JP2.8, JP7.2
VMID: C7.1, IC2.3 (OUT), IC19.3 (IN+), IC19.5 (IN+), IC19.10 (IN+), IC19.12 (IN+), IC21.3 (IN+), IC21.5 (IN+), IC21.10 (IN+), IC21.12 (IN+), IC22.3 (IN+), IC22.5 (IN+), IC22.10 (IN+), IC22.12 (IN+), IC23.3 (IN+), IC23.5 (IN+), IC23.10 (IN+), IC23.12 (IN+), IC24.3 (IN+), IC24.5 (IN+), IC24.10 (IN+), IC24.12 (IN+), IC25.3 (IN+), IC25.5 (IN+), IC25.10 (IN+), IC25.12 (IN+), IC26.3 (IN+), IC26.5 (IN+), IC26.10 (IN+), IC26.12 (IN+), IC27.3 (IN+), IC27.5 (IN+), IC27.10 (IN+), IC27.12 (IN+), JP7.4
VOUT: JP7.1, U$3.28 (D)

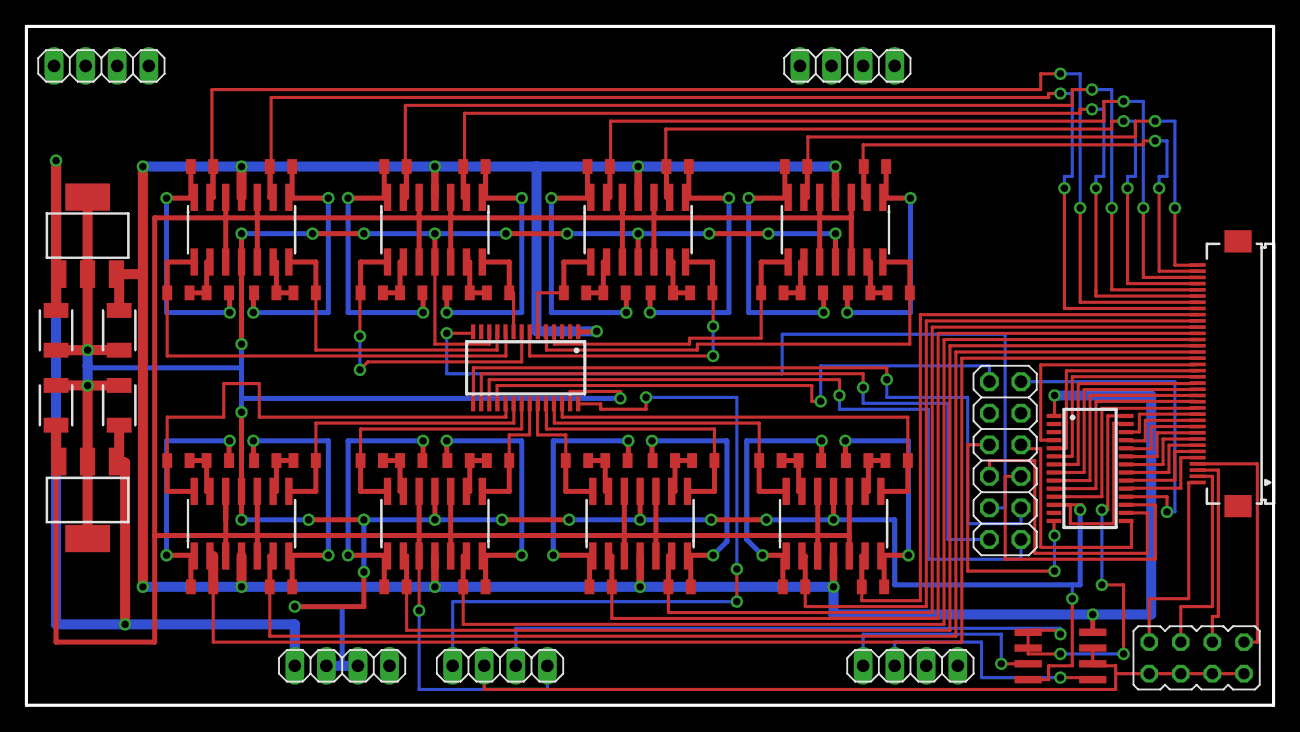
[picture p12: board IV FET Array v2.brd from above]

Board: 2 copper layers, 100.3 x 54.6 mm, 73 parts (0 on the bottom side), 103 nets.

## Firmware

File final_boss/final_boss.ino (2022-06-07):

//basically, run everything at once and see if anything breaks

#include <SPI.h>

#define VSPI_MISO   MISO
#define VSPI_MOSI   MOSI
#define VSPI_SCLK   SCK
//#define VSPI_SS     SS

#if CONFIG_IDF_TARGET_ESP32S2
#define VSPI FSPI
#endif

//uninitalised pointers to SPI objects
SPIClass * vspi = NULL;

static const unsigned long spiClk = 4000000; 

const int dacSelectPin = 5;
const int adcSelectPin = 2;
const int ldac = 4;

const int vgs_dac_channels [6] = {0, 1, 2, 3, 5, 6};   //address bits for gates 1-6 of the DAC
const float amps [3] = {1, 10.1, 20.1};
const int desired_amps [6] = {2, 2, 2, 2, 2, 2};    //0 for x1, 1 for x10, 2 for x20

const float test_resistor = 1000;  //resistor used to test transimpedance amp; placed between drain and source voltages

//source and drain mux pins
int drain_sel [5] = {12, 13, 14, 15, 16};   //pin 12 is the LSB, pin 16 is the MSB
int source_sel [5] = {21, 22, 25, 26, 27};  //pin 21 is the LSB, pin 27 is the MSB
const int drain_en = 17; //must be brought low to enable drain demultiplexer
const int source_en = 32; //must be brought low to enable source multiplexers

void setupDac() {
  vspi->beginTransaction(SPISettings(spiClk, MSBFIRST, SPI_MODE0));
  digitalWrite(dacSelectPin, LOW);
  vspi->transfer16(0b1 << 15);   //set up DAC with gain of 1, unbuffered on all channels
  //Serial.println(0b1 << 15);
  digitalWrite(dacSelectPin, HIGH);
  vspi->endTransaction();


  vspi->beginTransaction(SPISettings(spiClk, MSBFIRST, SPI_MODE0));
  digitalWrite(dacSelectPin, LOW);
  vspi->transfer16(0b1010000000000001);   //set up DAC with with LDAC high (default mode, so not needed), DAC outputs will not update until LDAC is pulsed low
  digitalWrite(dacSelectPin, HIGH);
  vspi->endTransaction();
  
}

void writeDac(unsigned int chan, unsigned int val) {
  vspi->beginTransaction(SPISettings(spiClk, MSBFIRST, SPI_MODE0));
  digitalWrite(dacSelectPin, LOW);
  vspi->transfer16(((0b111 & chan) << 12) + val);   //bits 14 through 12 for channel select, lower 12 bits for DAC data
  //Serial.println(((0b111 & chan) << 12) + val);
  digitalWrite(dacSelectPin, HIGH);
  vspi->endTransaction();
}

float readAdc() {
  word adc_stream;
  vspi->beginTransaction(SPISettings(spiClk, MSBFIRST, SPI_MODE0));
  digitalWrite(adcSelectPin, LOW);
  adc_stream = vspi->transfer16(0);   //read ADC data
  digitalWrite(adcSelectPin, HIGH);
  vspi->endTransaction();
  //Serial.println(adc_stream);
  //Serial.println((~(0b11 << 14) & adc_stream) >> 1);
  return (~(0b11 << 14) & adc_stream) >> 1;   //ignore the first two bits and the last bit of the adc data
}

void ldac_pulse() {
  digitalWrite(ldac, LOW);
  digitalWrite(ldac, HIGH);
}

//gate_or_source: 0 if drain, 1 if source
//channels are 0-indexed
void multiplexer(int address, bool drain_or_source) {
  int *select_bits;
  if (drain_or_source) {
    select_bits = source_sel;
  }
  else {
    select_bits = drain_sel;
  }

  for (int i = 4; i >= 0; i--) {
    if (address >= pow(2, i)) {
      digitalWrite(select_bits[i], HIGH);
      address -= pow(2, i); 
    }
    else {
      digitalWrite(select_bits[i], LOW);
    }
  }
}

void setup() {
  vspi = new SPIClass(VSPI);
  vspi->begin();
  
  Serial.begin(115200); //begin serial comms
  delay(500); //wait a bit (100 ms)

  pinMode(ldac, OUTPUT);
  pinMode(dacSelectPin, OUTPUT);
  pinMode(adcSelectPin, OUTPUT);
  digitalWrite(ldac, HIGH);
  digitalWrite(dacSelectPin, HIGH);
  digitalWrite(adcSelectPin, HIGH);

  pinMode(drain_en, OUTPUT);
  pinMode(source_en, OUTPUT);
  for (int i = 0; i < 5; i++) {
    pinMode(drain_sel[i], OUTPUT);
    pinMode(source_sel[i], OUTPUT);
  }

  digitalWrite(drain_en, LOW);  //enable the drain demultiplexer
  digitalWrite(source_en, LOW); //enable the source multiplexer
  for (int i = 0; i < 5; i++) {
    digitalWrite(drain_sel[i], LOW);
    digitalWrite(source_sel[i], LOW);
  }
  
  setupDac();
}

void loop() {
  for (int i = 0; i <= 10; i++) {

    int vds_bin = 400 * i;  //sweep Vds from 0V to 1V (offset by 1V since source voltage is 1V)
    float vds = vds_bin/4096.0*2.0;
    
    writeDac(4, vds_bin - 35);  //channel 4 is for Vds raw, offset of about 10 mV
    ldac_pulse();
    Serial.println();
    Serial.println("DAC output: " + String(vds));
    Serial.println("Expected Current: " + String((vds - 1.0)/test_resistor*1000, 4) + " mA");
    
    multiplexer(31, 0);
    multiplexer(0, 1);


    float transimp_out = readAdc()/4096.0 * 2.0;
    Serial.println("ADC voltage reading: " + String(transimp_out, 4));
    Serial.println("Measured Current: " + String((1.0 - transimp_out), 4) + " mA");

    Serial.println();
    for (int gate = 0; gate < 6; gate++) {
      
      int voltage_binary = i*50*(gate+1);
      int offset = 0;
      if ((gate == 4 || gate == 5) && (voltage_binary >= 20)) {
        offset = 20;
      }
      
      float true_voltage = ((voltage_binary/4096.0*2.0 - 1)*amps[desired_amps[gate]]) + 1;
      writeDac(vgs_dac_channels[gate], voltage_binary - offset); 
      Serial.println("Gate " + String(gate+1) + ": " + String(true_voltage));
    }
    ldac_pulse();
  
    delay(4000); 
  }

}

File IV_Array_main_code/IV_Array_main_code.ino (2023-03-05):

#include <Arduino.h>
#include <SPI.h>
#include <string.h>

//use ESP32 VSPI pins
#define VSPI_MISO   MISO
#define VSPI_MOSI   MOSI
#define VSPI_SCLK   SCK

//function definitions
String sweep(float vds, float* vgs);
void setupDac();
void writeDac(unsigned int chan, unsigned int val);
float readAdc();
void ldac_pulse();
int v_to_bin(float voltage);
float bin_to_v(int bin);
void multiplexer(int address, bool drain_or_source);
void copy(float* src, float* dst, int len);

//uninitalised pointers to SPI objects
SPIClass * vspi = NULL;

static const unsigned long spiClk = 800000;  //SPI clock frequency

//ADC and DAC pins
const int dacSelectPin = 5;    //slave select for DAC
const int adcSelectPin = 2;    //slave select for ADC
const int ldac = 4;            //pulse LDAC low to update DAC outputs all at once
const int vgs_dac_channels [6] = {0, 1, 2, 3, 5, 6};   //DAC channels for gates 1-6
const int vds_dac_channel = 4;   //DAC channel for drain

//gate voltage amplification
const float amps [3] = {1, 10.1, 20.1};             //amplification choices for each gate
const int desired_amps [6] = {0, 0, 0, 0, 0, 0};    //0 for x1, 1 for x10, 2 for x20
//NOTE: changing the values in desired_amps will not actually change the gate amplification, only the print output 
//is changed. The jumpers on the board determine the amplification for each gate.

//sweep parameters
float VGS_SWEEP_RATE = 0;  //VGS sweep rate in ms
float VDS_HOLD = 0;       //VDS_hold at beginning of sweep
int numReadings = 100;  //number of readings taken for each FET in the array
int numDummy = 5;     //number of dummy reads done beforehand
float VMID = 1;               //offset voltage for VGS and VDS

//Vgs parameters for gates 1 through 6
float VGS_START [6] = {-0.5, -0.5, -0.5, -0.5, -0.5, -0.5};       
float VGS_STOP [6] = {0.5, 0.5, 0.5, 0.5, 0.5, 0.5};
float VGS_INC [6] = {10e-3, 10e-3, 10e-3, 10e-3, 10e-3, 10e-3};
float VGS_OFFSETS [6] = {0, 0, 0, 0, 9e-3, 9e-3};  //positive offset means the DAC outputs a higher-than-expected value
float vgs [6];    //VGS as a value from -1 to 1V
int vgs_bin [6];  //VGS as a value from 0 to 4095

//Vds parameters
const float VDS_START = 800e-3;
const float VDS_STOP = 800e-3;
const float VDS_INC = 5e-3;
float VDS_OFFSET = 19e-3; //positive offset means the DAC outputs a higher-than-expected value
float vds;     //VDS as a value from -1 to 1V
int vds_bin;   //VDS as a value from 0 to 4095 (0V = 0, 2V = 4095)

//source and drain mux pins
int drain_sel [5] = {12, 13, 14, 15, 16};   //pin 12 is the LSB, pin 16 is the MSB
int source_sel [5] = {21, 22, 25, 26, 27};  //pin 21 is the LSB, pin 27 is the MSB
const int drain_en = 17; //must be brought low to enable drain demultiplexer
const int source_en = 32; //must be brought low to enable source multiplexers

const bool big_chip = 1;   //true if large chip is being used (6 gates, 32 source/32 drain)

String message;    //Serial print message

int powers_of_two [5] = {1, 2, 4, 8, 16};

void setup() {
  vspi = new SPIClass(VSPI);
  vspi->begin();
  
  Serial.begin(115200); //begin serial comms
  delay(1000); //wait a bit (1000 ms)

  pinMode(ldac, OUTPUT);
  pinMode(dacSelectPin, OUTPUT);
  pinMode(adcSelectPin, OUTPUT);
  pinMode(drain_en, OUTPUT);
  pinMode(source_en, OUTPUT);
  for (int i = 0; i < 5; i++) {
    pinMode(drain_sel[i], OUTPUT);
    pinMode(source_sel[i], OUTPUT);
  }
  
  digitalWrite(ldac, HIGH);          //initialize DAC and ADC control pins
  digitalWrite(dacSelectPin, HIGH);
  digitalWrite(adcSelectPin, HIGH);
  digitalWrite(drain_en, LOW);  //enable the drain demultiplexer
  digitalWrite(source_en, LOW); //enable the source multiplexer
  for (int i = 0; i < 5; i++) {
    digitalWrite(drain_sel[i], LOW);
    digitalWrite(source_sel[i], LOW);
  }
  
  setupDac();

}

void loop() {
  
  int i = 0;
  int j = 0;
  for(vgs[0] = VGS_START[0]; vgs[0] <= VGS_STOP[0]+0.5*VGS_INC[0]; vgs[0] = vgs[0] + VGS_INC[0]) {i++;} // determining data array size for exporting
  for(vds = VDS_START; vds <= VDS_STOP+0.5*VDS_INC; vds = vds + VDS_INC) {j++;}
  Serial.println("256," + String(i) + "," + String(j));

  //outer loop for Vds sweep, inner loop for Vgs sweep
  for(vds = VDS_START; vds <= VDS_STOP+0.5*VDS_INC; vds = vds + VDS_INC) {    // added 0.5*VDS_INC just in case VDS is not exactly precise and the loop terminates early
    
    vds_bin = v_to_bin(vds - VDS_OFFSET);  // convert desired voltage into appropriate binary value (0 to 4095)
    writeDac(vds_dac_channel, vds_bin);
    ldac_pulse();                         //update DAC output

    for (int gate = 0; gate < 6; gate++) {
      vgs[gate] = VGS_START[gate];
    }
    
    while(vgs[0] <= VGS_STOP[0]+0.5*VGS_INC[0]) {  // added 0.5*VGS_INC just in case VGS is not exactly precise and the loop terminates early

      for (int gate = 0; gate < 6; gate++) {
        vgs_bin[gate] = v_to_bin(vgs[gate] - VGS_OFFSETS[gate]);             // convert desired voltage into appropriate binary value (0 to 4095)
        writeDac(vgs_dac_channels[gate], vgs_bin[gate]);                    // write DAC value to 1 of the 6 gates
      }
      
      
      if(vgs[0] == VGS_START[0]) {delay(VDS_HOLD);}
      else {delay(VGS_SWEEP_RATE);}                             // delay to allow EDL to reach steady state
      ldac_pulse();
      
      message = sweep(vds,vgs);
      Serial.print(message); 

      for (int gate = 0; gate < 6; gate++) {
        vgs[gate] += VGS_INC[gate];
      }
    }
  }
  
  Serial.println("END");
  
}

String sweep(float vds, float* vgs) {
  unsigned long t1;
  int vmeas_bin_avg = 0;
  int vmeas_bin = 0;
    
  String message = "";

  t1 = millis();
  message += String(t1);
  
  message += ",";
  message += String(vds,4);                        // gives VDS with 4 decimals of precision
  message += ",";

  for (int gate = 0; gate < 6; gate++) {
    float vgs_amped = vgs[gate]*amps[desired_amps[gate]];
    message += String(vgs_amped,4);                        // gives VGS with 4 decimals of precision
    message += ",";
    break;   //only once for now
  }
  
  message += String(VMID);
  message += ",";
  
  int multiplexer_max = big_chip ? 32 : 16;        //if big chip is being used, there are 32 drains/sources; small chip only has 16
  
  for (int vds_select = 0; vds_select < multiplexer_max; vds_select++) {   
    for (int vmeas_select = 0; vmeas_select < multiplexer_max; vmeas_select++) {      
      multiplexer(vds_select, 0);
      multiplexer(vmeas_select, 1);
      
      vmeas_bin_avg = 0;
      
      for (int i = 0; i < numDummy; i++) { //perform some dummy reads to let the currents settle
        readAdc();   
      }  

      for (int i = 0; i < numReadings; i++) { //actual readings
        vmeas_bin = readAdc();
        vmeas_bin_avg += vmeas_bin; 
      }
      
      vmeas_bin_avg = vmeas_bin_avg / numReadings;

      //for 0 to 4095 integer output
      //message += String(vmeas_bin_avg);

      //for -1 to 1 float output
      float vmeas_avg = bin_to_v(vmeas_bin_avg);
      message += String(vmeas_avg, 4);

      message += ",";
    }
  }
  message = message.substring(0, message.length() - 1);  // removes the last comma so that when comma delimited we have an array with 256 elements and not 257
  message += "\n";
  return message;
}

//Note: The DAC (AD5328) operates in SPI Mode 1 (data is sampled on the falling edge of the clock)
void setupDac() {

  vspi->beginTransaction(SPISettings(spiClk, MSBFIRST, SPI_MODE1));
  digitalWrite(dacSelectPin, LOW);
  vspi->transfer16(0b1 << 15);   //set up DAC with gain of 1, unbuffered on all channels
  digitalWrite(dacSelectPin, HIGH);
  vspi->endTransaction();


  vspi->beginTransaction(SPISettings(spiClk, MSBFIRST, SPI_MODE1));
  digitalWrite(dacSelectPin, LOW);
  vspi->transfer16(0b1010000000000001);   //set up DAC with with LDAC high (default mode, so not needed), DAC outputs will not update until LDAC is pulsed low
  digitalWrite(dacSelectPin, HIGH);
  vspi->endTransaction();
}

//Note: The DAC (AD5328) operates in SPI Mode 1 (data is sampled on the falling edge of the clock)
void writeDac(unsigned int chan, unsigned int val) {
  vspi->beginTransaction(SPISettings(spiClk, MSBFIRST, SPI_MODE1));
  digitalWrite(dacSelectPin, LOW);
  vspi->transfer16(((0b111 & chan) << 12) + val);   //bits 14 through 12 for channel select, lower 12 bits for DAC data
  digitalWrite(dacSelectPin, HIGH);
  vspi->endTransaction();
}

//Note: The ADC (MCP3201) operates in SPI Mode 0 (data is sampled on the rising edge of the clock)
float readAdc() {
  word adc_stream;
  vspi->beginTransaction(SPISettings(spiClk, MSBFIRST, SPI_MODE0));
  digitalWrite(adcSelectPin, LOW);
  adc_stream = vspi->transfer16(0);   //read ADC data
  digitalWrite(adcSelectPin, HIGH);
  vspi->endTransaction();
  return (~(0b11 << 14) & adc_stream) >> 1;   //ignore the first two bits and the last bit of the adc data
}

void ldac_pulse() { //used to update DAC output
  digitalWrite(ldac, LOW);
  digitalWrite(ldac, HIGH);
}

//converts a Vds or Vgs voltage from -1 to 1V to an integer from 0 to 4095
int v_to_bin(float voltage) {
  int bin;
  voltage = voltage + VMID;
  bin = int(voltage / (2*VMID) * 4096 );
  bin = min(max(0, bin), 4095);  //enforce limits of 12-bit binary number
  return bin;
}

//converts an integer from 0 to 4095 to a voltage from -1 to 1V
float bin_to_v(int bin) {
  float voltage;
  voltage = (bin / 4096.0 * 2*VMID) - VMID;
  voltage = min(max(-VMID, voltage), VMID); 
  return voltage;
}
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

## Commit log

2022-03-22 added PCB
    [ESP32+DAC.SchDoc, FPCs.SchDoc, Gate_Protection.SchDoc, Gate_Protection.~(16).SchDoc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]
2022-04-03 incorporated Jaeyoung's design
    [Connectors.SchDoc, ESP32+DAC.SchDoc, FPCs.SchDoc, IV_Array.PrjPcb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]
2022-04-04 changed to LT1945, 1v ref LDO
    [ESP32+DAC.SchDoc, IV_Array.PrjPcb, Measure.SchDoc, Measure_Source.SchDoc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]
2022-04-05 aded thresholds back, added testpoints, created top level sheet
    [1825255-1.PcbLib, 1825255-1.SchLib, Connectors.SchDoc, ESP32+ADC+DAC.SchDoc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]
2022-04-06 switched -20V and +20V around
    [Power.SchDoc, Top_Level.SchDoc]
2022-04-09 changed to 0805 components
    [Connectors.SchDoc, ESP32+ADC+DAC.SchDoc, Measure.SchDoc, PCB1.PcbDoc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]
2022-04-13 layout of components, testing DAC SPI code with multiple SPI slaves
    [ESP32+ADC+DAC.SchDoc, Power.SchDoc, Transmit.SchDoc]
2022-04-20 routed everything except multiplexers
    [ESP32+ADC+DAC.SchDoc]
2022-04-21 routed multiplexers to small connector
2022-04-26 added global switch and 80- and 60-pin connectors
    [Connectors.SchDoc, Transmit.SchDoc]
2022-04-26 finished routing, no drc errors
    [Connectors.SchDoc, IV_Array.PrjPcb]
2022-04-28 random stuff: changing 0603's to 0805, changing out transimp amp, etc
    [Assembly Testpoint Report for PCB1.csv, Bill of Materials-IV_Array.xlsx, Connectors.SchDoc, IV_Array.PrjPcb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]
2022-04-28 made interface board
    [Large_Connector_Interface.PrjPcb, Large_Interface_Connector.PrjPcb, PCB1.PcbDoc, Sheet1.SchDoc]
2022-05-01 boost converter shutdown control, silk, and rounded corners
    [IV_Array.PrjPcb, Large_Connector_Interface.PrjPcb, PCB1.PcbDoc, Power.SchDoc]
2022-05-01 generated gerbers
    [Assembly Testpoint Report for PCB1.csv, Bill of Materials-IV_Array.xlsx, Bill of Materials-Large_Connector_Interface.xlsx, IV_Array.PrjPcb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]
2022-05-02 committing before messing with internal layers
    [Bill of Materials-IV_Array.xlsx, PCB1.GBL, PCB1.GBO, PCB1.GBP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]
2022-05-03 increased via size from 20 to 24 mils
    [Bill of Materials-IV_Array.xlsx, PCB1.GBL, PCB1.GBO, PCB1.GBP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]
2022-06-07 updated test code
    [Bill of Materials-Large_Connector_Interface.xlsx, Large_Connector_Interface.PrjPcb, PCB1.GBL, PCB1.GBO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]
2023-02-07 massive file update
    [Adafruit HUZZAH32 ESP32 Feather.brd, Adafruit HUZZAH32 ESP32 Feather.sch, Breathalyzer_ESP32.PrjPcb, Breathalyzer_GateAmp.PrjPcb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]
2023-02-11 added testpoints to PCBs, and global gate switch
    [Breathalyzer_Power+ICs.PrjPcb, ESP32.SchDoc, Mux+Conn.SchDoc, PCB1.PcbDoc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]
2023-02-14 finalized new iv_array code, also fixed DRC errors on ESP32 board
    [Breathalyzer_ESP32.PrjPcb, ESP32.SchDoc, PCB1.PcbDoc]
2023-02-14 started routing the second board
    [PCB1.PcbDoc, Power+ICs.SchDoc]
2023-03-05 added humidity sensor, heater circuit, rerouted
    [Breathalyzer_Boost.PrjPcb, ESP32.SchDoc, PCB1.PcbDoc, Power+ICs.SchDoc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]
2023-03-12 started routing bottom board
    [Breathalyzer_Power+ICs.PrjPcb, ESP32.SchDoc, Mux+Conn.SchDoc, PCB1.PcbDoc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]
2023-03-28 PCBs nearing completion
    [Breathalyzer_80_Interface.PrjPcb, Breathalyzer_Boost.PrjPcb, Breathalyzer_Mux+Conn.PrjPcb, Breathalyzer_Mux+Conn_Small.PrjPcb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]
2023-03-29 PCBs finalized, main change was JST battery connector flip
    [Breathalyzer_80_Interface.PrjPcb, ESP32.SchDoc, Mux+Conn.SchDoc, PCB1.PcbDoc]
2023-04-05 generated gerbers, also started writing new code
    [Breathalyzer_ESP32.PrjPcb, Breathalyzer_Power+ICs.PrjPcb, ESP32.SchDoc, _PCB PN_.GBL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]
2023-04-10 some changes to boost pcb (moving r1, adding silk)
    [PCB1.PcbDoc]
2023-05-23 file reorg
    [1825255-1.PcbLib, 1825255-1.SchLib, Adafruit HUZZAH32 ESP32 Feather.brd, Adafruit HUZZAH32 ESP32 Feather.sch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]
2023-05-23 added test plan, power flow, and drawing
    [New Microsoft Excel Worksheet.xlsx, New PCB Test Plan.xlsx, PCB1.~(51).PcbDoc]
2023-05-31 added old PCB stuff from Charles
    [IV FET Array v2.brd, IV FET Array v2.sch, New Microsoft Excel Worksheet.xlsx, New PCB Test Plan.xlsx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]

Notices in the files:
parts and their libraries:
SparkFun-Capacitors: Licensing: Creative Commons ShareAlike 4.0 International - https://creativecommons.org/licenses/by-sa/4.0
